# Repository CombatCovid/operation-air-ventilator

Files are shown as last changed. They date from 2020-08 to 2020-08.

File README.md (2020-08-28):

# OperationAIR - Assist In Respiration

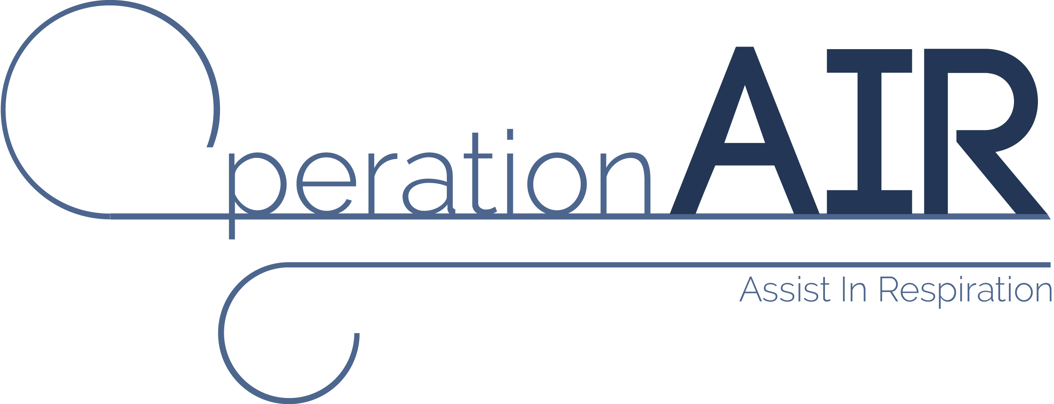
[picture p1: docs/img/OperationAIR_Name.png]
OperationAIR_Name


## OperationAIR: Who are we?

OperationAIR is a student team of Delft University of Technology that developed a simplified ventilator: the AIRone. It was developed as a non-certified, advanced emergency ventilator at times of a national shortage due to the covid-19 pandemic, in close contact with experts from Leiden University Medical Center and Erasmus Medical Center.

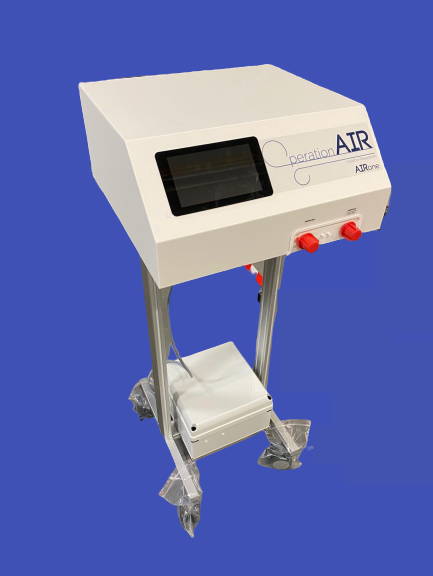
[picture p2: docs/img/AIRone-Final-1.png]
AIRone-Final-1


## AIRone: What is it?

The AIRone operates and functions as a regular, pressure-regulated  ventilator, but with essential functionalities only. In short, it uses a pressurised gas source, reduces the pressure accordingly and delivers  gas to the patient by a set of proportional valves (see below for more  details). Oxygen concentration is regulated using two Mass Flow  Controllers on the gas inlets.

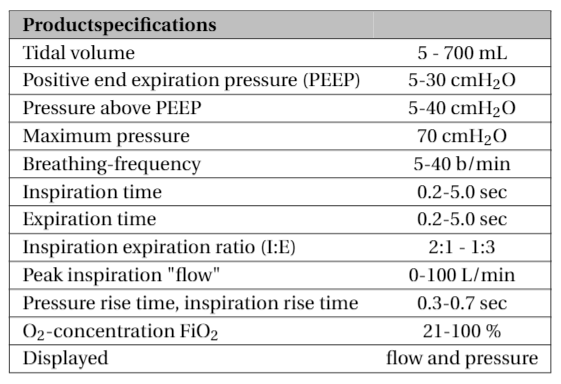
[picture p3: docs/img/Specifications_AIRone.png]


The  AIRone provides positive-pressure ventilation (PPV) for emergency  automatic ventilation, created for the use on adult (suspected) COVID-19 patients who need non-weaned respiratory support to bridge a longer  period of time until conventional ventilation becomes available.

## Adjustable settings

- Inspiratory pressure (Pinsp)
- Positive end-expiratory pressure (PEEP)
- Respiratory rate (RR)
- I:E ratio
- Oxygen concentration(%) (FiO2)

## Project Motivation

The design of the AIRone is final. As national ICU admissions are  dropping large scale production is not necessary. The AIRone is  currently being produced in a small batch to complete the design cycle  and to share this expertise with the international community. Software  engineers will continue to work on an additional module to enable  patient respiration triggers for weaning.

The AIRone was recommended by clinicians to be used at times of  national shortage of certified ventilators. Official approval has not  been obtained, due to the disappeared urgency of emergency ventilators.  Therefore, the safety or efficacy of the AIRone for use in humans has  not been proven. However, thorough design verification was performed  using an advanced artificial test lung. Additionally, design  documentation is under review by a notified body. Also, multiple  usability tests by doctors and nurses lead to the current user-friendly  design.

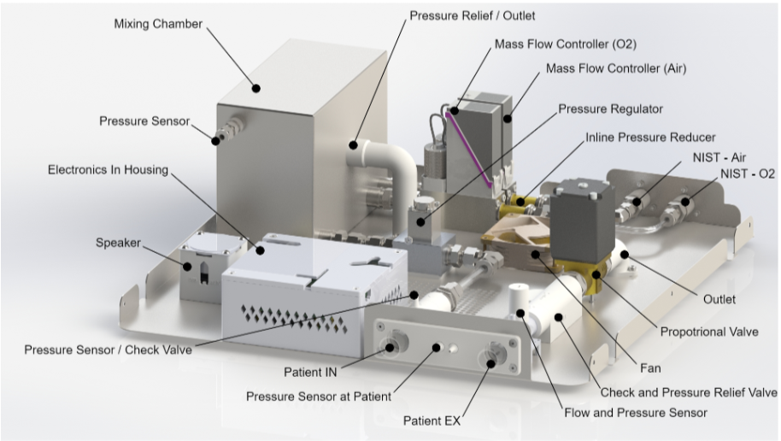
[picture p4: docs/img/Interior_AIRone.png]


## General Working Principle

The AIRone uses pressurized medical air and oxygen that is available  in most Dutch hospitals, reduces it to the required pressure, and  delivers this to the patient using a set of proportional valves that are controlled using a central microcontroller.

The physician can start up the device and use the touchscreen (GUI)  to set ventilation parameters to the desired settings. The GUI will  communicate these setting to the MicroController Unit (MCU). The MCU  then controls all valves to ventilate the patient accordingly.

The AIRone has two male NIST (Non-interchangeable screw thread)  connectors, one for compressed medical air and one for oxygen. The  female counterparts of these connectors should be available in the Dutch hospital and can be connected to the AIRone. The input pressure of both oxygen and compressed air may vary between 4 and 8 bar. In the device,  the oxygen and air pressure is reduced to 4 bar. Two Mass Flow  Controllers (MFCs) are used to control the flow of both gasses into a  mixing chamber. This ensures a highly controlled mixing ratio, having a  gas with the desired oxygen concentration as result. A pressure sensor  in the mixing chamber gives feedback to the MFCs, adjusting their flow  to keep the pressure in the chamber at 650 mbar. As a back-up, a back  pressure regulator ensures the pressure in the chamber will never exceed 1 bar by blowing off air when the pressure is too high.

Downstream of the mixing chamber, a proportional valve regulates the  pressure going into the patient. Generally, the valve will open at the  start of inspiration and close when the pressure at the lungs is at the  desired plateau pressure.  Before the gas mixture flows to the patient  it passes a check valve which blocks flow coming back from the patient.

During expiration, the gas is filtered by a HEPA filter. The gas then passes another check valve, and also a pressure relief valve, which  opens when the pressure in the system rises above 70 cmH20. The gas is  then released to outside the system by another proportional valve that  opens at the beginning of the expiration and closes at the end of the  expiration.

------

**Be aware this design explicitly focuses on use in the Dutch  healthcare infrastructure. Alterations of this design will be needed for local implementation. Please leave your contact information and  additional information in this form so we can discuss matters or offer  advice and support:** https://forms.gle/rWXyzbqTNrqdJqee8

## DISCLAIMER

Licensor means Technische Universiteit Delft and OperationAIR. Licensee means any business, organisation or person using the Licensed Material. Licensed Material means all information pertaining to the last resort ventilator also known as the AIRone

### Intended use

1. The AIRone is a last resort device. It is not designed to replace the currently available, conventional ventilators. The AIRone is a pressure-controlled emergency mechanical ventilation system created for the treatment of COVID-19 patients, who need respiratory support, for who no conventional ventilation machine is available. 
2. The for profit exploitation of the Licensed Material is explicitly prohibited.

### Disclaimer of Warranties and Limitation of Liability.

The Licensor offers the Licensed Material “as-is” and “as-available”, and makes no representations or warranties of any kind concerning the Licensed Material, whether express, implied, statutory, or other. This includes, without limitation, warranties of title, merchantability, fitness for a particular purpose, non-infringement, absence of latent or other defects, accuracy, or the presence or absence of errors, whether or not known or discoverable.

To the extent possible, in no event will the Licensor be liable to Licensee on any legal grounds (including, but not limited to, gross negligence and wilful misconduct) or otherwise for any direct, special, indirect, incidental, consequential, punitive, exemplary, or other losses, costs, expenses, or damages arising out of this Public License or use of the Licensed Material, even if the Licensor has been advised of the possibility of such losses, costs, expenses, or damages.

The disclaimer of warranties and limitation of liability provided above shall be interpreted in a manner that, to the extent possible, most closely approximates an absolute disclaimer and waiver of all liability.

## Project Organization

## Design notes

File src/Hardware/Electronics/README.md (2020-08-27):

# Electronics and firmware for Operation Air Ventilator

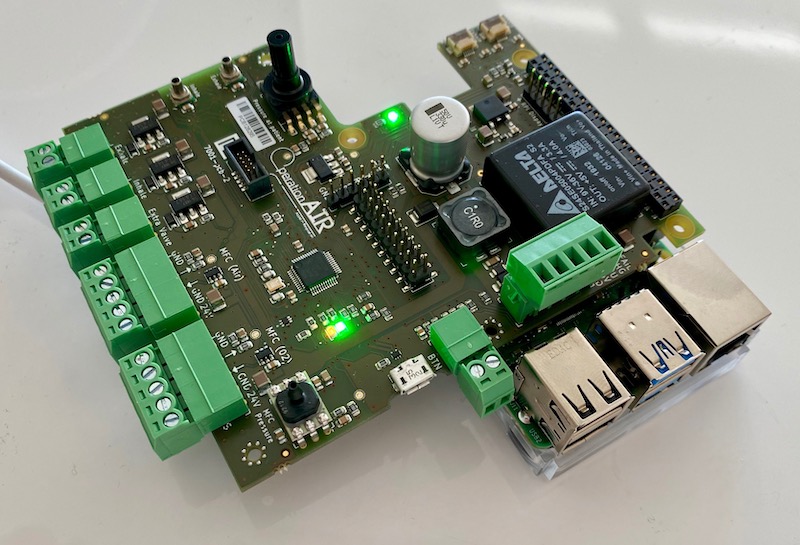
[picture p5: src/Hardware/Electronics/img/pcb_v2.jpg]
OperationAir PCB


The electronics for the Operation Air AIROne is comprised of a custom developed PCB with a LPC11U37 microcontroller stacked on top of a Raspberry Pi 4 (Model B).

This repository contains the electronic designs for the PCB and the accompanying firmware.

The Pi talks to the microcontroller over UART using a [custom binary protocol](firmware/README.md#uart-communication-protocol).

Contact info@interay.com for assembled, tested and programmed ready for use boards.

## License

Copyright (c) 2020 TU Delft. All rights reserved.

Licensed under the [Apache 2.0](LICENSE) license.

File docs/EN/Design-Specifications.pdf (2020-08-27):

| Design Specifications
OPERATIONAIR: OperationAIR (OperationAIR) | Date: 2020/04/29 14:28:23
Document: 1 | Page: 1 / 12

All dates and times are in the project’s default time zone and formatting.

### 1. TABLE OF CONTENTS

### 2. DESIGN SPECIFICATIONS

### 2.0.1. Features

SPEC-31 Ventilation mode
Device has a Pressure Controlled Ventilation (PCV) mode

SPEC-46 Usability user-interface
The user-interface is intuitive, simple, and straightforward to use

SPEC-34 Visualized measurements
Volume [mL], pressure [cm H2O] and flow [L/min] must be visualized on the device's screen in graphs or as numbers

SPEC-150 Instructions For Use
Instructions For Use (IFU) are supplied with every device and are available for download online

SPEC-42 Compatibility with standard hospital equipment
The device is compatible with standard hospital equipment according to NEN-EN-ISO 5359:2014/A1:2017 and ISO 5361:2016

SPEC-141 Inspiratory hold

(OperationAIR) | Date: 2020/04/29 14:28:23
Document: 1 | Page: 2 / 12

The device can perform an inspiratory hold to determine Plateau Pressure.
When the button is pressed, respiration stops at the peak of the inspiration, while measuring the pressure in the system. When the user lets go of the button, respiration instantly starts again

SPEC-156 Expiratory Hold
The device can perform an expiratory hold to determine PEEP.
When the button is pressed, respiration stops at the end of the expiration, while measuring the pressure in the system. When the user lets go of the button, respiration instantly starts again

SPEC-73 Interruption of power supply
Device is equipped with a UPS to continue ventilation in case of power failure

SPEC-60 Breaks
The device has breaks that shall be used when the device doesn't need to be moved

SPEC-27 Flow Sensor
Device must be equipped with a flow sensor

SPEC-153 HEPA filter
Device can be equipped with a HEPA filter

SPEC-25 HME-filter
Device must be equippable with an ISO 9360-1:2000 certified HME-filter and should be equipped with such a HME filter. These HME filters are disposable and must be changed with every patient.

SPEC-166 Ventilator
The device has a ventilator to mix potential leaking oxygen with surrounding air

### 2.0.1.1. Ventilation Parameters

SPEC-155 Ppeak setting
The pressure above PEEP can be set by the user in the range 5 to 40 cm H2O, in intervals of 1 cm H2O

(OperationAIR) | Date: 2020/04/29 14:28:23
Document: 1 | Page: 3 / 12

SPEC-35 PEEP setting
The positive end-expiratory pressure (PEEP) must be adjustable between 5 and 30 cm H2O, and the PEEP can be adjusted per 1 cm H2O

SPEC-20 Breathing rate setting
The breathing rate can be set by the user between 5/min and 40/min

SPEC-38 I:E ratio setting
Inspiratory:expiratory ratio must be adjustable between 2:1 and 1:3

SPEC-37 FiO2 setting
The FiO2 must be adjustable per 5%

### 2.0.1.2. Alarms

SPEC-6 Alarm for Inspiratory O2 concentration (FiO2)
An alarm for a too high or too low fractional inspiratory oxygen level.

SPEC-9 Alarm for positive end-expiratory pressure (PEEP)

SPEC-8 Alarm for Tidal volume (Tv)
Provide an alarm when the tidal volume is outside the accepted range set by the user.

SPEC-89 Alarm for Peak Pressure (Ppeak)

SPEC-87 Alarm for Apnea or disconnect
Alarm when inspiratory or expiratory airflow circuit is blocked or disconnected

SPEC-84 Alarm for empty battery
Device issues a warning when battery is almost empty.

(OperationAIR) | Date: 2020/04/29 14:28:23
Document: 1 | Page: 4 / 12

SPEC-19 Clear explanation per alarm on GUI
When an alarm or warning is issued, the device must clearly indicate what alarm is issued

### 2.0.2. Performance

SPEC-95 Error margins: Tidal Volume
Maximum error between internally and externally measured Tidal Volume is 5%

SPEC-94 Error margins: I:E ratio
Maximum error between set and measured I:E ratio is 0.05

SPEC-93 Error margins: FiO2
Maximum error margin between measured and set FiO2 is 5%

SPEC-92 Error margins: breating rate
Maximum error between measured and set breating rates is 1/min

SPEC-90 Error margins: Lung/airway pressure
Maximum pressure loss between device and patient lungs is 10 cm H2O

SPEC-36 FiO2 range
Device is able to provide a FiO2 between 21% and 100% at 5% accuracy.

SPEC-26 Tidal Volume
Device is able to provide tidal volumes between 300 and 700 mL

SPEC-40 Inspiratory Flow
The inspiratory flow that the device delivers to the patient has a peak value of at least 1.5 L/s

SPEC-118 Reliability
Under the same settings the device should give the same output.

(OperationAIR) | Date: 2020/04/29 14:28:23
Document: 1 | Page: 5 / 12

SPEC-128 14 day reliability
Device must be able to operate continuously for at least 14 days, preferably more. Specify expected durability in documentation.

### 2.0.3. Safety

SPEC-29 Peak pressure
Device must keep the peak pressure always below 70 cm H2O

SPEC-146 Flow sensor shielding
Flow sensor is electrically shielded, all components near the flow sensor are non-conductive or sufficiently grounded

SPEC-144 Airflow materials
All components through which inspiratory air can flow are
- biocompatible
- oxygen compatible
- clean
- non-porous
- have a high auto-ignition temperature

SPEC-129 Robustness
The device is able to withstand continous use and transport

SPEC-126 Cleaning and disinfection
The device and its materials are able to withstand regular cleaning and disinfection

SPEC-120 Alarms are easy to understand and intuitive
The alarms are made according to ISO 60601-1-8

SPEC-113 Impairment of cooling

(OperationAIR) | Date: 2020/04/29 14:28:23
Document: 1 | Page: 6 / 12

The medical device must remain safe during the failure of cooling systems, f.e. when ventilation openings are covered.

SPEC-103 No air leakage
The device may not leak air or oxygen

SPEC-100 External exhaust outlets
External exhaust outlets are placed in the bottomplate of the device, where they cannot be blocked by walls or other objects

SPEC-99 Temperature of inspirated air
Temperature of the inspirated air and the tubes through which the air flows must be below 30 degrees celcius

SPEC-85 High Voltage circuit outside casing
The high voltage circuitry shall be separated from the high O2 network

SPEC-83 Testing of the fail-safe valve during production
The correct functioning of fail-safe valves shall be tested during production

SPEC-80 Housing impact test
The housing must withstand an impact of a solid smooth steel ball, approximately 50 mm in diameter and with a mass of 500 g ± 25 g, falling freely from 1,3 m height once onto each relevant part of the test sample or swinging like a pendulum, that drops through a vertical distance of 1,3 m, against vertical surfaces. The test is not applied to flat panel displays.

SPEC-79 Housing mechanical resistance
The housing must be able to withstand forces of 250 N without breaking

SPEC-72 Leakage current testing
Since the protective earthing is accessible, leakage current is considered touch current, and the acceptance level for leakage current is <100 uA.

(OperationAIR) | Date: 2020/04/29 14:28:23
Document: 1 | Page: 7 / 12

SPEC-71 Patient leakage current
The values for patient leakage must not exceed 50 uA

SPEC-70 Touch current
Touch current from or between parts of the medical device within the patient environment must not exceed 100 μA. Leakage current from accessible outer surfaces of the equipment is also considered to be touch current.

SPEC-67 Acoustic Energy
The acoustic energy emitted by the device shall not exceed 80 dB during worst case normal use

SPEC-65 Sharp edges
The device shall have no sharp edges that could lead to tearing of protective gloves or the skin

SPEC-63 Instability unintended force
The device must be able to withstand unintended forces without tipping over.

SPEC-62 Instability incline surface
Device must not overbalance when placed on an inclined surface at 10 degrees from the horizontal

SPEC-143 Visibility User Interface
The user interface can be easily used and is clearly visible when wearing protective eyewear

SPEC-145 Watchdog program
A watchdog program checks every second if every part of the software does what it is supposed to do. When a part of the software malfunctions, the watchdog will instruct a different part to reboot the malfunctioning part.

SPEC-53 Power Supply
The device shall use a IEC 60601-1 certified mains supply adapter for connection to a 230V AC supply mains.

(OperationAIR) | Date: 2020/04/29 14:28:23
Document: 1 | Page: 8 / 12

SPEC-32 Expirated air
The expirated air must always be separated from inpiratory air

SPEC-44 Non-conductive exterior casing
The exterior casing of the device must be made of a non-conductive material or the material must be grounded

SPEC-45 Protective equipment
The device can be used by users wearing personal protective equipment such as gloves and protective glasses

SPEC-23 Protected off switch
The off switch is protected for accidental pressing

SPEC-22 The O2 and air input connectors
The O2 and air input connectors comply with ISO 18082:2014 and are non-interchangeable

SPEC-18 Battery use warning
When power supply fails and the device starts running on battery power, an alarm is issued

SPEC-5 Pressure relief valve
The device has a mechanical pressure relief valve that opens at 70 cm H2O

SPEC-4 Calibrate sensors during assembly
All pressure sensors and the flow sensor must be calibrated during assembly

SPEC-2 Robustness internal components
All internal components are tightly secured to the bottomplate

SPEC-1 Ingress of water
The exterior casing is spraying water proof (comparable with IP-22)

(OperationAIR) | Date: 2020/04/29 14:28:23
Document: 1 | Page: 9 / 12

SPEC-162 Installation Verification
Installation Verification is performed after assembly:
- Serial numbers of components have to be registered
- The power supply has to be inspected
- The device has to be inspected visually
- Pressure sensors have to be inspected
- The device has to be turned on and off and power down has to be inspected
- Electrical safety has to be inspected
- Sensors, valves and output have to be tested
- Gas system integrity has to be tested.

### 2.0.4. Information provided to the user

### 2.0.4.1. IFU

SPEC-152 IFU: regulatory requirements
The medical device must be accompanied by an IFU with referral address of the manufacturer. These documents can be shared electronically or in printing. Additionally the following must be included:
- a list of all items that are part of the medical device,
- instructions for installation, assemblation and modification,
- instructions for cleaning, desinfection, sterilization of each item or the entire device,
- the safety measures that should be applied during installation,
- which parts are suited for the patient environment,
- Measures that must be applied during preventive maintenance,
- the permissible environmental conditions of use of the ME SYSTEM including conditions for transport and storage,
- advice to the RESPONSIBLE ORGANIZATION: – to carry out all adjustment cleaning, sterilization and disinfection PROCEDURES specified therein;
- advice to the RESPONSIBLE ORGANIZATION: – that the assembly of ME SYSTEMS and modifications during the actual service life require evaluation to the requirements of this standard.
- the name of the device;
- the manufacturer of the device;
- the adress of the manufacturer;
- Indications and contra-indications,
- intended use and intended user;
- the clinical benefit for the patient;
- the performance characteristics;
- the degree of accuracy for the parameters of the device;
- how to verify if the right accessories are used;
- undesirable side-effects;

(OperationAIR) | Date: 2020/04/29 14:28:23
Document: 1 | Page: 10 / 12
- preperation of the device before use;
- that users must receive a training before using the device;
- information on maintenance and cleaning of the device and accessories;
- information on cleaning and disinfection between the use on different patients;
- all the warnings that will lead to malfunction of the device and/or changes in the working of the device that will lead to risks to the patient. This will include enviromental changes, like diagnostic or therapeutic procedures;
- how the device can safely be disposed;
- publication or printing date with version number;
- that SAE's must be meantioned to the manufacturer;
- how to safely use the software on the device.

SPEC-47 IFU: intended use
IFU contains an explanation of the intended use of the device

SPEC-13 IFU: Device not for use during transport
Warning in IFU that the device may not be used during patient transport

SPEC-14 IFU: Check device before use
Warning in IFU that device functionality must be checked before use

SPEC-98 IFU: Do not use when damaged
Instructions For Use mention that the device must be inplugged when damaged, for example after a fall or when other parts are visibly damaged.

SPEC-117 IFU: turn off device before unplugging
Warning in the IFU that the device has to be turned off on the user interface before cutting the power

SPEC-134 IFU: ventilator settings
The IFU mentions the upper and lower limits of the ventilation settings

SPEC-135 IFU: Explanation of the alarms
The alarms, their causes, and how to deal with them should be clearly explained in the IFU.

(OperationAIR) | Date: 2020/04/29 14:28:23
Document: 1 | Page: 11 / 12

SPEC-137 IFU: HEPA filter
The IFU contains instructions about the use of the HEPA-filter

SPEC-51 IFU: Instructions for correct and safe maintanance
The instructions for use shall state instructions for correct and safe maintenance

SPEC-138 IFU: alarm boundaries
The IFU explains how to set the upper and lower alarm boundaries and mentions the alarm limits

SPEC-17 Training and clear IFU for the users
IFU and training materials are developed and validated in collaboration with medical doctors and nurses. IFU warns that the device can only be used by trained users.

SPEC-49 IFU: checked by experts
The Instructions for use shall be reviewed by both internal quality control and external experts

### 2.0.4.2. Label

SPEC-151 Label: regulatory requirements The label on the device will contain:
- the device name;
- a serial number;
- the manufacturer with address;
- the manufacturing date, as part of the serial number or seperatly;
- immediate warnings with icons.
All will be written in text or official icons.

SPEC-64 Emergency use sticker
The device has a clear warning sticker with the text that it is a device which is meant for use ONLY in emergencies on COVID-19 patients.

(OperationAIR) | Date: 2020/04/29 14:28:23
Document: 1 | Page: 12 / 12

SPEC-115 Emergency number on label
A telephone number is shown on the label that can be called when assistance is required

SPEC-133 HEPA filter warning sticker
Sticker above the expiratory air connector of the device with the text that the HEPA filter must be placed before use

SPEC-61 Do not push warning
The label has a warning to not push (ISO 7010 P017).

SPEC-154 Fire warning sticker
The label contains a warning to keep device away from open fire

SPEC-148 Device label
The label is placed on the device and must be visible from the point of use by the user.

SPEC-130 Intuitive for use - training
Must not require more than 30minutes training for a doctor with some experience of ventilator use.

SPEC-48 Vocabulary and Semantics
Always use the standard nomenclature as defined in BS ISO 19223:2019 regarding lung ventilators and related equipment: Vocabulary and semantics.

SPEC-167 Open Source
All documentation of the AIRone is online available for free. When documentation goes missing or is unreadable, the user can refer to the online database.

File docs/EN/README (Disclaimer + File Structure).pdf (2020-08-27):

## README

DISCLAIMER

Licensor means Technische Universiteit Delft and OperationAIR

Licensee means any business, organisation or person using the Licensed Material

Licensed Material means all information pertaining to the last resort ventilator also known as the AIRone

Intended use

1. The AIRone is a last resort device. It is not designed to replace the currently available, conventional ventilators. The AIRone is a pressure-controlled emergency mechanical ventilation system created for the treatment of COVID-19 patients, who need respiratory support, for who no conventional ventilation machine is available.
2. The for profit exploitation of the Licensed Material is explicitly prohibited.

Disclaimer of Warranties and Limitation of Liability.

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

## OSF File Structure - OperationAIR

- README (Disclaimer + File Structure)
- General
- Instructions for Use
- Service Structure
- Team Structure
- Tips and Pitfalls
- Hardware
- AIRone Assembly
- Architecture
- Bill Of Materials
- Design Specifications
- Design Verification
- Technical Manual
- Assembly Manuals
■ 1. Work Instructrion Subassembly 1 - MFC-AIR_EN
■ 2. Work Instruction Subassembly 2 - MFC-OXYGEN_EN ■ 3. Work Instruction Subassembly 3 - Mixing chamber_EN ■ 4A. Work Instruction Subassembly 4A - Swagelok_EN ■ 4B. Work Instruction Subassembly 4B - 3D blocks_EN ■ 4C. Work Instruction Subassembly 4C - Insp_Tract_EN ■ 5. Work Instruction Subassembly 5- Expiratory Tract_EN ■ 6. Work Instruction Subassembly 6 - PCB + wiring_EN
■ 6B. Work Instruction Subassembly 6B- SD_software_EN ■ 6C. Work Instruction Subassembly 6C- SD_connection_EN ■ 7. Work Instruction Subbassembly 7 - Hood_EN
■ 8. Work Instruction Subassembly 8 - Bottom plate_EN
■ 9. Work Instruction Subassembly 9 - Trolley_EN
■ 10. Work Instruction Subassembly 10 -Connect components _ Components to plate_ EN
■ 11. Work Instruction Subassembly 11 - Wiring_EN
■ 12. Work Instruction Subassembly 12 - Bottom plate + trolley_EN ■ 13. Work Instruction Subassembly 13 - hood_to_base_EN
■ 14. Work Instruction Subassembly extra - speaker_EN
- Hardware Overviews
■ Connector-G1-2_22mm
■ Connector-G3_8-22mm
■ Overview_Interior
■ Overview_Interior_3D_Printing ■ Overview_Exterior
■ Selection_Cover_Closed
■ Selection_Cover_EX
■ Selection_Inspiratory_EX ■ Selection_Speaker_Double

- 3D Printing
■ 3D Printing Overview
■ FDM_Electronics_Housing_1 ■ FDM_Electronics_Housing_2 ■ FDM_EX_Pressure_Relief_Plate ■ FDM_Flow_Sensor_Cap
- Renders
■ Airchain
■ Airchain_EX
■ Cap_Back
■ Cap_Front
■ Expiration
■ Expiration_EX
■ Exterior
■ Exterior_Front_Back
■ Inspiration
■ Inspiration_3Dprint
■ Inspiration_3Dprint_EX
■ Inspiration_EX
■ Inspiration_incl_3Dprint ■ Interior
■ Interior_Exterior
■ Interior_Top
■ Interior_Trolley
■ NIST_Bottom
■ NIST_Bottom_EX
■ NIST_Bottom_Rear
■ O2chain
■ O2chain_EX
■ PCB
■ PCB_EX
■ Pin
■ Pin_EX
■ Plate
■ Plate_AIR
■ Plate_Connections
■ Plate_Expiration
■ Plate_Fan
■ Plate_Inspiration
■ Plate_O2
■ Plate_Patient_Connection
■ Plate_Patient_Connection_EX ■ Plate_Tank
■ Plate_Tank02
■ Plate_Top
■ Speaker
■ Speaker_EX

■ Tank
■ Tank_EX
■ Trolley
■ Trolley_EX
- Software
- Human Interface
■ Github Human Interface
- Electronics
■ Github Electronics

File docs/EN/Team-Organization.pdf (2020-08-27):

Management:
Professor
Team manager (student)
3 Subteam leaders

Phase One (Week 1 to 3.5)

Team Leader: (external framework, valves, testing, O2) | Vice-Team Leader: (software, GUI, 3D and control)
1 | 1
External framework & Connections | Mixing chamber
3D ontwerpers | Test team
Software design | Interface/GUI
Control (systems) | Valves
Team members: valves | Team members: external framework | Team members: 3D team | Team members: software
3 | 3 | 6 | 3
Team members: O2 sensor | Team members: test team | Team members: control | Team members: interface/GUI
1 | 4 | 4 | 2

Design subteams

## Design

Phase One (Week 1 to 3.5) | Realisation

Team Leader
1
Production | Implementation | Distribution
Explore production facilities | Manual | Packaging parts/device
Find manufacturers for parts | Maintenance | Shipment
Who will assemble the product? | Education of clinical staff | Contact with national center coordination center for distribution
Where do we assemble? | Installation plan | Provide (or advise on) compatible disposables to be used with device
Sterilization? | Control of device
Post-production quality check
Team members | Team members | Team members
2 | 3 | 3

Phase One (Week 1 to 3.5) | PR & Legal & Finance

Team Leader
1
Media & PR | Finance | Legal
Put out requests for parts critical of elivery | Calculate cost/device | Risk management
Maintain media contact | Plan finance for upscaling | Risk mitigation plan
Update social media platforms and create website | | Test protocol
Create platform to spread information about our project | | Test plan
| | Distribute responsibility, reliability and authorities
Team members | Team members | Team members
2-4 | 2 | 5

Management
Professor
1 Team manager (student)
3 Subteam leaders
1 Workshop manager

Phase Two (Week 3.5 to now)

Team leader: 1 (Hardware) | Team leader
Vice Team leader: 1 (Software) | 1
Team | Development | Troubleshooting | Support team | Durability monitoring
| Software updates | Be present in clinic during first use | Answer emergency phone | Monitor quality of devices
| Control systems update | Standby for troubleshooting | Answer service phone | Monitor life cycle parts
| 3D design update | Name incidents and propose solutions | Collect incident reports | Create service plan
| Patient triggers | Install devices hen first used | Post reports and update user FAQ | Test seperate models on durability
| Hardware update | Quickfix software bugs | Overview team member part experts
| | | pass user feedback to the right sub team
Team members | Team members | Team members | Team members
14 | 8 | 5 | 6

Phase Two (Week 3.5 to now)

Media & PR | Open Source | International contacts
Put out requests for parts critical of elivery | Document project | Provide consultation to other teams
Maintain media contact | Open Source | Answer questions to other initiatives
Update social media platforms and create website
Create platform to spread information about our project
Team members | Team members | Team members
2 | 5 (part time) | 5 (part time)

Phase Two (Week 3.5 to now)

Team leader
1
Supplychain management | Logistics | Training coordination
Maintain contact with part manufacturers | Overview ventilator locations | Train the education team
Mediate between assebly company and part manufacturers | Overview locations of education and service teams | Update user manual
Plan deliveries | Overview logistics of part delivery | Update education material
Solve problems regardng delayed parts | Overview transport of teams to hospitals | Coordinate post-market training
Maintain contact with Dutch health authorities | Maintain contact with national distribution network for health supplies
Create traceability plan for assembly
Team members | Team members | Team members
4 | 3 | 3

Phase Two (Week 3.5 to now)

Training team | Production | Finances
Give training to users | Assist with assembly | Request funding of funds
| | Request funding of grants
Team members | Team members | Team members
9 | 7 | 1
| Extra members during start-up fase
| 6

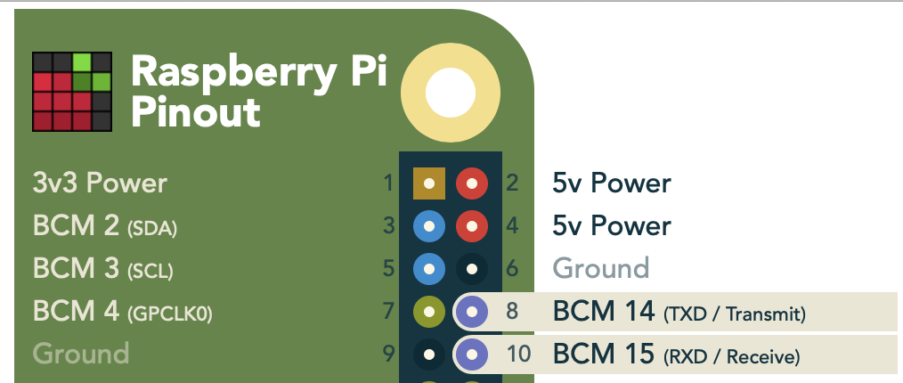
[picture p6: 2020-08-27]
src/Hardware/Electronics/blinky/img/uart_pinout.png

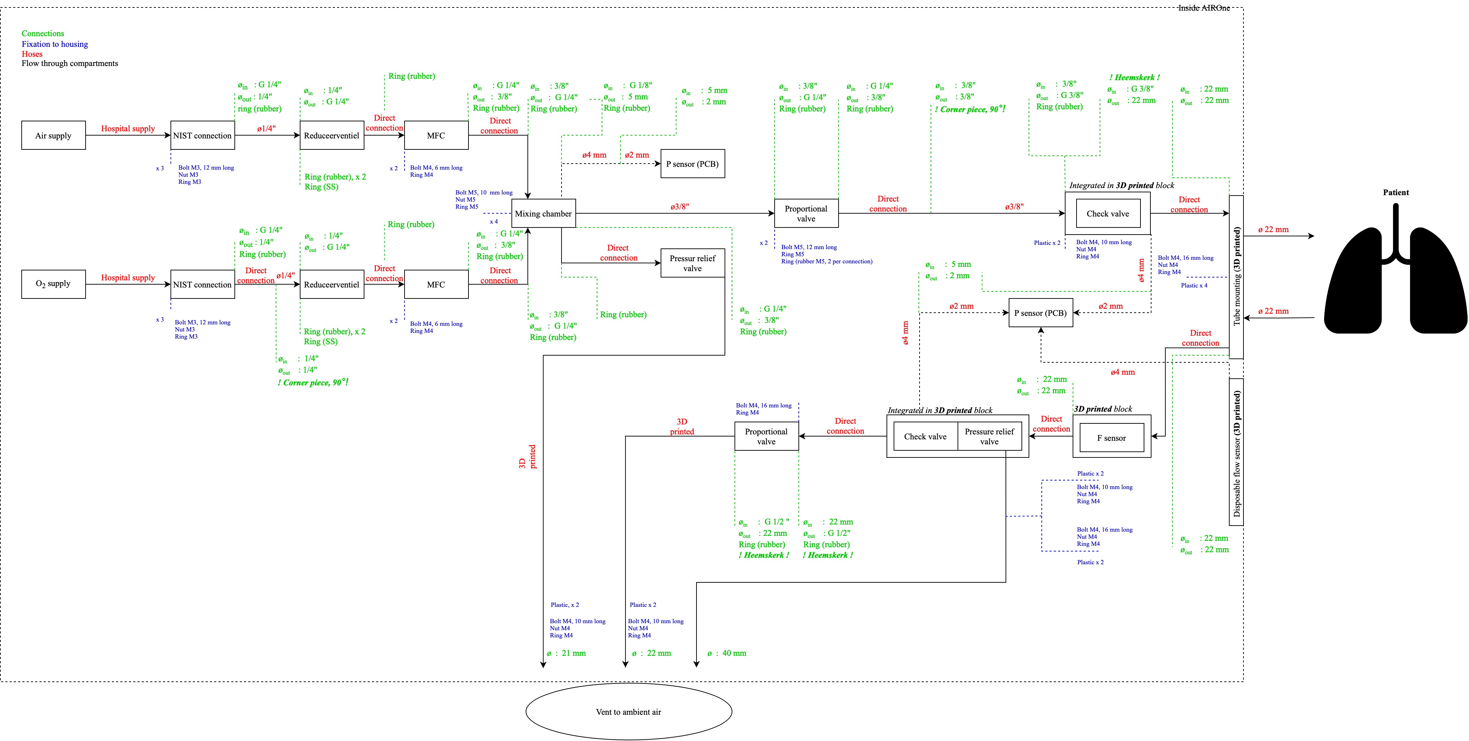
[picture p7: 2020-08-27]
docs/img/Architecture.jpg

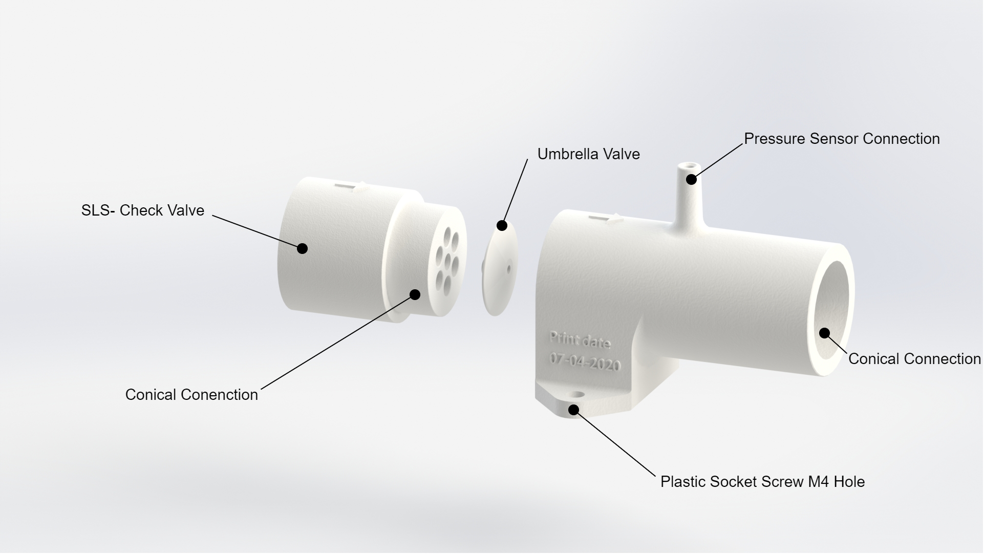
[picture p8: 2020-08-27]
src/Hardware/Hardware-Overview/Selection_Inspiratory_EX.png

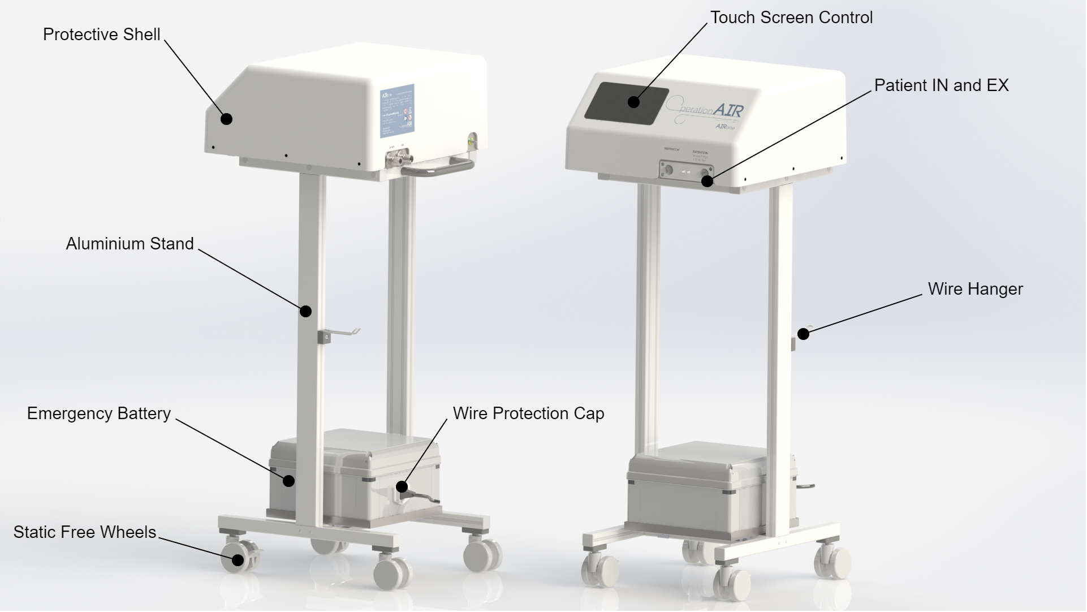
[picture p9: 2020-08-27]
src/Hardware/Hardware-Overview/Overview_Exterior.png

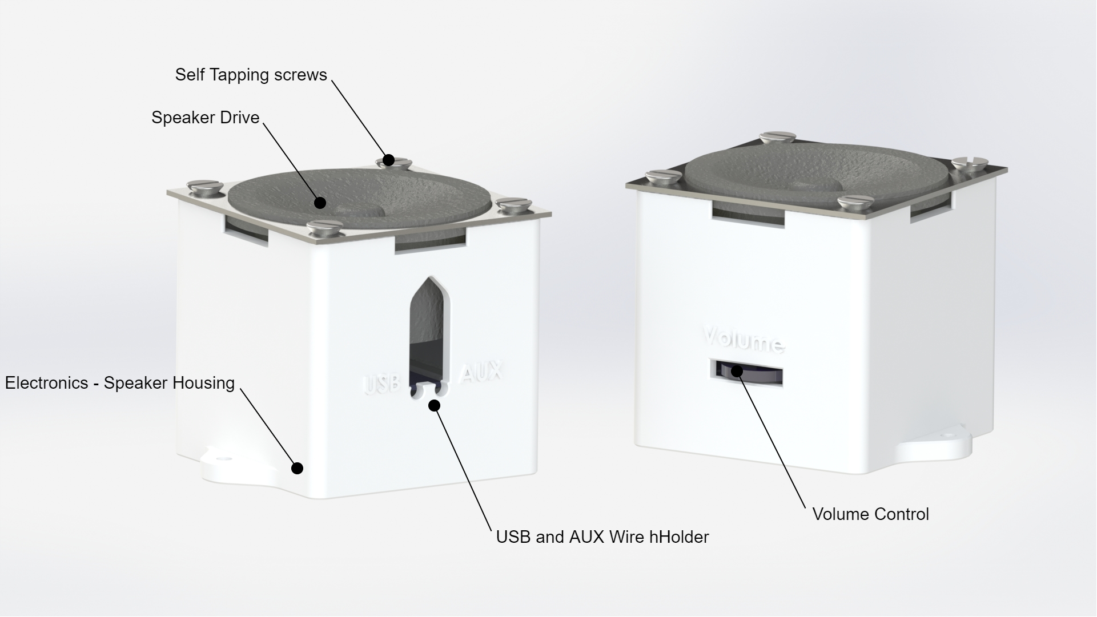
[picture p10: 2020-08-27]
src/Hardware/Hardware-Overview/Selection_Speaker_Double.png

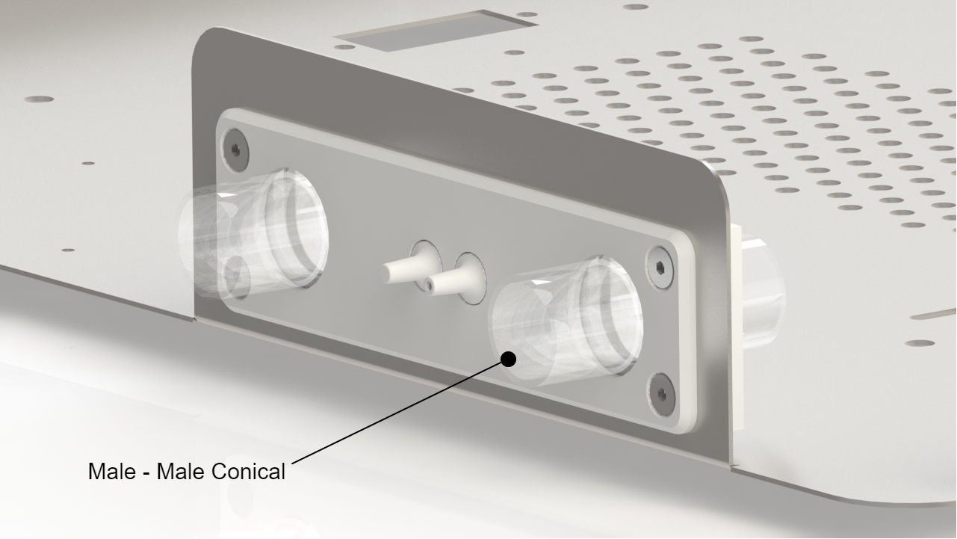
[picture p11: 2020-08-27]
src/Hardware/Hardware-Overview/Selection_Cover_Closed.png

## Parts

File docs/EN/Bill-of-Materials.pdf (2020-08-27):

BOM Level | Part-ID | Part Name | Quantity | Technical Requirement Notes | OperationAIR Suppliers
0 | 0 | AIRone, Packed | 1 | Mechanical ventilator
1 | 1 | Electronic control system | 1
2 | 1.1. | Assembled PCB | 1 | Link to Github: https://github.com/OperationAIR/electronics See the Technical Manual (4.17) for detailed specifications | Interay Solutions
3 | 1.1.1. | Pressure Sensors | 1 | | Interay Solutions
4 | 1.1.1.1 | Pressure Sensor 1 | 1 | MPVZ5010GW6U See the Technical Manual for detailed specifications | Interay Solutions
4 | 1.1.1.2 | Pressure Sensor 2 | 1 | MPRLS0001PG0000SA See the Technical Manual for detailed specifications | Interay Solutions
4 | 1.1.1.3 | Pressure Sensor 3 | 1 | ABPDANT015PGAA5 See the Technical Manual for detailed specifications | Interay Solutions
3 | 1.1.2 | PCB printing parts | 1 | | Interay Solutions
3 | 1.1.3 | PCB Base Plate | 1 | | Würth Elektronik GmbH & Co. KG
3 | 1.1.4 | Software | 1 | | Jitter
2 | 1.2 | Raspberry Pi | 1 | Raspberry Pi 4 4G Model B See the Technical Manual (4.18) for detailed specifications | RS online
2 | 1.3 | Raspberry Pi Touchscreen Display | 1 | Raspberry Pi 7" 800x480 DSI Touchscreen Display See the Technical Manual (4.18) for detailed specifications | RS online
2 | 1.4 | Micro-SD Card (16G) | 1 | Kingston 16 GB MicroSDHC Card Class 10, UHS-1 U1 | RS online
2 | 1.5 | High pressure hoses | 1
3 | 1.5.1 | High pressure hose 1 | 2 | 4mm, PVC 4x6mm | Landfeld
3 | 1.5.2 | High pressure hose 2 | 1 | 4mm, 6x1 mm | Festo
3 | 1.5.3 | High pressure hose 3 | 3 | 2mm, 3x0.5mm | Festo
3 | 1.5.4 | High pressure hose connector | 3 | Adapter, PP, Male luer to 1/16" barbed | Interscience
2 | 1.6 | Cables | 1
3 | 1.6.1 | Jumper Cable | 1 | 6876 FFC, 0.5mm Pitch, 6 Way, 200mm Cable Length, 500 mA, 60 V ac | RS online
3 | 1.6.2 | Flex cable Raspberry Pi to Camera Board | 1 | 30 cm, MPN: 2283 | Kiwi electronics
3 | 1.6.3 | Cable PCB to Solenoid Control Valve | 1 | 10cm, 0.3255mm2 (22 AWG), 2 cable cores
3 | 1.6.4 | Cable PCB to ARMAND klep | 1 | 40cm, 0.3255mm2 (22 AWG), 2 cable cores
3 | 1.6.5 | Cable PCB to Raspberry Pi | 1 | USB IDC connection cable, 45cm, 24 AWG, 5 cable cores, F-F connections
3 | 1.6.6 | Cable PCB to Power cable | 1 | 20cm, 1.3087 mm2 (16 AWG), 5 cable cores
2 | 1.7 | Aluminum tape | -
2 | 1.8 | Ferrite cores | 1
3 | 1.8.1 | Ferrite core: cable PCB to MFC | 1 | TDK Openable Ferrite Clamp, 16.5 Dia. x 30mm | RS online
3 | 1.8.2 | Ferrite core: cable PCB to flow sensor | 1 | 28R0480-000 - Ferrite Ribbon Core, 190 ohm, 100 MHz, 8.0mm x 1.0mm | Farnell
3 | 1.8.3 | Ferrite core: cable PCB to Raspberry Pi | 1 | Wurth Elektronik 4 W 1500 Ferrite Sleeve, Inner dimensions:18.8 x 1.1mm | Farnell
2 | 1.9 | Grounding cable | - | Grounding for cables 30cm, 2.5mm2 (AWG14)
2 | 1.1 | Heatshrink | - | 1 mm diameter
2 | 1.11 | Speaker | 1 | Nedis - CSPR10020BK See the Technical Manual (4.19) for detailed specifications | TodoTipo
2 | 1.12 | Grounding | 1 | | Medical IT Shop
3 | 1.12.1 | Grounding pin | 1 | Potential Equalization Pin Built in Plug Complete 6/15 | Medical IT Shop
3 | 1.12.2 | Grounding cable | 1 | DIN 42801, PE Connection Lead STD 6mm² / 3m | Medical IT Shop
2 | 1.13 | Power Supply | 1 | See the Technical Manual (4.23) for detailed specifications
3 | 1.13.1 | Power Cable | 1 | Power Cable C13 | Medical IT Shop
3 | 1.13.2 | Transformer | 1 | Meanwell 200W Reliable Green Medical Power Supply, RPS-200-24 | Telerex

3 | 1.13.3 | UPS | 1 | Meanwell Supply40ADC UPS Module, DR-UPS40 | Telerex
3 | 1.13.4 | Battery | 1 | DYN/DAS12-2.2 | NS
1 | 2 | Housing | 1 | See the Technical Manual (4.22) for detailed specifications
2 | 2.1 | Metal bottom plate | 1 | Custom design | Kasteelmetaal
2 | 2.2 | Top cap | 1 | Custom design | Formit
2 | 2.3 | Sealing cap | 1 | Intersurgical reference number: 1978000 | Merkala
2 | 2.4 | Chassis | 1 | Custom design | Item
2 | 2.5 | Stickers | 1 | Custom design | Sticker Koning
3 | 2.5.1 | Technical Sticker | 1 | Custom design | Sticker Koning
3 | 2.5.2 | Safety Sticker | 1 | Custom design | Sticker Koning
3 | 2.5.3 | Inlet / outlet stickerset | 1 | Custom design | Sticker Koning
3 | 2.5.4 | Logo sticker | 1 | Custom design | Sticker Koning
1 | 3 | Mechanic | 1
2 | 3.1 | Mass flow controler | 1 | | Bronkhorst
3 | 3.1.1 | MFC AIR including cables | 1 | OAD-001F See the Technical Manual (4.3) for detailed specifications | Bronkhorst
3 | 3.1.2 | MFC O2 including cables | 1 | OAD-002F See the Technical Manual (4.3) for detailed specifications | Bronkhorst
2 | 3.2 | Gas pipe fittings | 1 | See the Technical Manual (4.23) for detailed specifications | Swagelok
3 | 3.2.1 | G1/4" to 3/8" tube ftting | 6 | SS-600-1-4RS | Swagelok
3 | 3.2.2 | G1/4" to 1/4" tube fitting | 4 | SS-400-1-4RS | Swagelok
3 | 3.2.3 | G3/8" to 3/8" tube fitting | 1 | SS-600-1-6RS | Swagelok
3 | 3.2.4 | Elbow 1/4" | 1 | SS-400-2R-4 | Swagelok
3 | 3.2.5 | Elbow 3/8" | 1 | SS-600-2R-6 | Swagelok
3 | 3.2.6 | G1/8" Gasket | 1 | SS-2-RS-2V | Swagelok
3 | 3.2.7 | G1/4" Gasket | 16 | SS-4-RS-2V | Swagelok
3 | 3.2.8 | G3/8" Gasket | 1 | SS-6-RS-2V | Swagelok
3 | 3.2.9 | G1/2" Gasket | 1 | SS-8-RS-2V | Swagelok
3 | 3.2.10 | G1/4" to 3/8 tube fitting | 2 | SS-6-TA-1-4RS | Swagelok
3 | 3.2.11 | G1/8" to 6mm | 1 | SS-6M0-1-2RS | Swagelok
2 | 3.3 | PFA Tubing | 1 | | Swagelock
3 | 3.3.1 | PFA Tubing 3/8" | - | PFA_T6_062_100 | Swagelock
3 | 3.3.2 | PFA tubing 1/4" | - | PFA-T4-047-100 | Swagelock
2 | 3.4 | Solenoid Control Valve (Expiratory) | 1 | Type 2875 - Direct-acting 2 way standard solenoid control valve See the Technical Manual (4.16) for detailed specifications | Burkert
2 | 3.5 | Spring loaded overpressure relief valve | 1 | 70-250 mbar, Part number 5046, DN40KF See the Technical Manual (4.15) for detailed specifications | Demaco
2 | 3.6 | Safety Valve | 1 | Mini safety valve G 1/4", 1 - 4 bar, Brass, Item number: SVM 14-4 See the Technical Manual (4.6) for detailed specifications | Landefeld
2 | 3.7 | Umbrella Valve | 2 | UM 215.002 SD See the Technical Manual (4.8+4.14) for detailed specifications | Minivalve
2 | 3.8 | SLS 3D prints | | Printed with Nylon 12
3 | 3.8.1 | Patient IN | 1 | Custom design: housing umbrella valve | Shell
3 | 3.8.2 | Patient OUT | 1 | Custom design: housing umbrella valve, pressure sensor, pressure relief | Shell
3 | 3.8.3 | Check valve mount | 2 | Custom design: mount for umbrella valve, placed on Patient IN/OUT | Shell
3 | 3.8.4 | Pressure tubes | 1 | Custom design: mount for pressure tubes, placed in tube doublemount | Shell

3 | 3.8.5 | Flow sensor holder | 1 | Custom design: housing flowsensor | Shell
3 | 3.8.6 | EndTube | 1 | Custom design: leads expiratory air outside the device | Oceanz
3 | 3.8.7 | Tankout | 1 | device | Oceanz
2 | 3.9 | Diamond Dichtol | - | Dichtol WFT standard #1532 | Leering
2 | 3.1 | Glue Loctite | - | Loctite super glue 4061 | Eriks
2 | 3.11 | Connector G3/8" - 22M | 1 | Custom design | Heemskerk
2 | 3.12 | Connector G1/2" - 22M | 2 | Custom design | Heemskerk
2 | 3.13 | Flow sensor | 1 | 0-100 L/min, 24V, max 6W See the Technical Manual (4.12) for detailed specifications | VPinstruments
2 | 3.14 | Mixing chamber | 1 | Custom design See the Technical Manual (4.4) for detailed specifications | RPP
2 | 3.15 | Proportional Inhalation Valve | 1 | Model: PCS-FV-010-EV-IV. Inlet pressure: 0.1-1 bar gauge. Outlet pressure: 0-0.15 bar gauge. Max operating pressure: 1 bar gauge. Orifice Size: 4,5 mm See the Technical Manual (4.7) for detailed specifications | Pressure control solutions
2 | 3.16 | Pressure regulator | 2 | DRV1340 Pressure regulator 4bar See the Technical Manual (4.2) for detailed specifications | Kramp
2 | 3.17 | FDM 3D prints | 1 | Printed with PLA (polylactic acid)
3 | 3.17.1 | Tube doublemount | 1 | Custom design: mount on bottom plate to fixate inspiratory and expiratory tubes and pressure tubes | MTB3D
3 | 3.17.2 | Flow sensor protection | 1 | Custom design: cap to protect flow sensor | MTB3D
3 | 3.17.3 | Pressure relief print | 1 | Custom design: plate to fixate pressure relief to bottom plate | MTB3D
3 | 3.17.4 | Elektronics cover | 1 | Custom design: housing for electronics | MTB3D
3 | 3.17.5 | Elektronics roof | 1 | Custom design: roof for electronics cover | MTB3D
3 | 3.17.6 | Speaker print | 1 | Custom design: housing for speaker | MTB3D
3 | 3.17.7 | Cover | 1 | Custom design: cover for front of the tube doublemount | MTB3D
3 | 3.17.8 | FlowsensorBasket | 1 | Custom design: fixation of flow sensor to bottom plate | MTB3D
2 | 3.18 | Ventilator | 1 | Noctua NF-A8 5V PWM USB 80mm Fan See the Technical Manual (4.20) for detailed specifications | Azerty
2 | 3.19 | NIST fitting O2 | 1 | Custom design See the Technical Manual (4.1) for detailed specifications | Heemskerk
2 | 3.2 | NIST fitting AIR | 2 | Custom design See the Technical Manual (4.1) for detailed specifications | Heemskerk
2 | 3.21 | 22mm-22mm connector | 2 | Intersurgical reference number: 1960000 See the Technical Manual (4.10) for detailed specifications | Merkala/Intersurgical
1 | 4 | Fasteners Mechanic - Housing | 1
2 | 4.1 | NIST air / NIST O2 | 1
3 | 4.1.1 | Bolt M3x12 | 6 | Steel
3 | 4.1.2 | Nut M3 | 6 | Steel
3 | 4.1.3 | Ring M3 | 6 | Steel
2 | 4.2 | MFC air / MFC O2 | 1
3 | 4.2.1 | Bolt M4x6 | 4 | Steel
3 | 4.2.2 | Ring M4 | 4 | Steel
2 | 4.3 | Mixing chamber | 1
3 | 4.3.1 | Bolt M5x10 | 3 | Steel
3 | 4.3.2 | Nut M5 | 3 | Steel
3 | 4.3.3 | Ring M5 | 3 | Steel
2 | 4.4 | Digital pressure regulator | 1
3 | 4.4.1 | Bolt M5x12 | 2 | Steel

3 | 4.4.2 | Ring M5 | 2 | Steel
3 | 4.4.3 | Laser cut plate for proportional inhalation valve | 1 | Custom design
2 | 4.5 | 3D printed components | 1
3 | 4.5.1 | Bolt M4x12 | 8 | Plastic
3 | 4.5.2 | Bolt M4x16 | 2 | Plastic
3 | 4.5.3 | Nut M4 | 14 | Plastic
3 | 4.5.4 | Ring M4 | 10 | Plastic
3 | 4.5.5 | M4x20 Countersunk screws | 4 | Plastic
2 | 4.6 | Solenoid Control Valve | 1
3 | 4.6.1 | Bolt M4x16 | 1 | Steel
3 | 4.6.2 | Ring M4 | 1 | Steel
2 | 4.7 | Speaker and electronics | 1
3 | 4.7.1 | M4x14mm Countersunk screws | 8 | Self tapping, steel
3 | 4.7.2 | Machine Screw M2.5x10 | 14 | DIN 7985, M2.5, 10 mm, Steel, Zinc, Recessed Pan Head Pozidriv
3 | 4.7.3 | Standoff M2.5x11 | 4 | Nickel Plated, Brass, M2.5, Hex Female, 11 mm, 11 mm
3 | 4.7.4 | Standoff M2.5x18 | 4 | Steel, M2.5, Hex Male-Female, 18 mm, 24 mm
3 | 4.7.5 | Standoff M2.5x30 | 3 | Steel, M2.5, Hex Female-Female, 30 mm
3 | 4.7.6 | Push-In Rivet | 6 | Black Nylon Fir Tree Push-In Rivet. Item code: 27MXT003006
3 | 4.7.7 | Screw M2.5x8 | 2 | DIN7500, M2.5, 8 mm, Zinc, Steel, Recessed Pan Head Pozidriv
3 | 4.7.8 | Tooth lock washer M4 | 7 | Steel
3 | 4.7.9 | Tooth lock washer M5 | 5 | Steel
3 | 4.7.10 | Ring Tongue terminal M4 | 3 | Ring Tongue terminal M4 2.5mm2
3 | 4.7.11 | Ring M2.5 | 7 | Steel
3 | 4.7.12 | Tooth lock washer M2.5 | 7 | Steel
2 | 4.8 | Top Cap | 1
3 | 4.8.1 | Push-In Rivet 1 | 6 | Black UL94 V-0 Nylon Round Snap Push-In Rivet, Item code: SRVO-4100B
1 | 5 | Manuals | 1
2 | 5.1 | Technical Manual | 1 | See 'Technical_Manual.pdf'
2 | 5.2 | Hand-out Instruction for User | 1
2 | 5.3 | Instructions for Use | 1 | See 'Instructions for Use.pdf'
1 | 6 | Packaging | 1
2 | 6.1 | Pallet and box | 1 | JOPAK
2 | 6.2 | Sticker | 1 | Stickerkoning

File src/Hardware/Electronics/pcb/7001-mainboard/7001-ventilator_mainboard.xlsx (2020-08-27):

Sync | Ref | Qty | Value | Footprint | MPN | Farnell | Mouser | Digikey
1 | R16, R17, R8, R9, | 4 | 0 | Resistor_SMD:R_0805_2012Metric |  | 2447574
1 | R5, R4, | 2 | 33R | Resistor_SMD:R_0805_2012Metric |  | 2447640
1 | R49, R50, R41, R42, R43, | 5 | 150 | Resistor_SMD:R_0805_2012Metric |  | 2747563
1 | R3, R12, R22, R24, R23, | 5 | 1k5 | Resistor_SMD:R_0805_2012Metric |  | 2447592
1 | R29, R40, R38, R19, R44, R37, R46, R45, | 8 | 3.3k | Resistor_SMD:R_0805_2012Metric |  | 2447651
1 | R34, R36, R32, R21, | 4 | 4.7k | Resistor_SMD:R_0805_2012Metric |  | 2447672
1 | R47, | 1 | 150 1% | Resistor_SMD:R_0805_2012Metric
1 | R48, | 1 | 2.32k 1% | Resistor_SMD:R_0805_2012Metric
 | ~~R48,~~ | ~~1~~ | ~~2.2k~~ | ~~Resistor_SMD:R_0805_2012Metric~~
1 | RV1, | 1 | Varistor | Jitter_Footprints:WE_VS_Varistor | 82551250
1 | R6, R35, R39, R15, R18, R11, | 6 | 10k | Resistor_SMD:R_0805_2012Metric |  | 2447553
1 | R31, R10, R1, R2, | 4 | 68k | Resistor_SMD:R_0805_2012Metric |  | 2447706
1 | R33, R14, R20, R13, | 4 | 100k | Resistor_SMD:R_0805_2012Metric |  | 2447551
1 | C10, C12, | 2 | 18pF | Capacitor_SMD:C_0805_2012Metric |  | 2821165
1 | C34, | 1 | 470pF | Capacitor_SMD:C_0805_2012Metric |  | 2409053
1 | C40, C20, C7, C35, C37, | 5 | 2.2nF | Capacitor_SMD:C_0805_2012Metric |  | 1414681
1 | C5, C6, C36, | 3 | 1nF | Capacitor_SMD:C_0805_2012Metric |  | 3013468
1 | C17, C45, C27, | 3 | 2.2nF 50V | Capacitor_SMD:C_0805_2012Metric |  | 1414681
1 | C46, C47, | 2 | 10nF 100V | Capacitor_SMD:C_1206_3216Metric | 885012208112
1 | C28, C29, C1, C23, C49, C2, C3, C21, C15, C50, C43, C8, C9, C31, C33, | 15 | 100nF | Capacitor_SMD:C_0805_2012Metric |  | 1650866
1 | C19, C39, C48, C51, C54, | 5 | 100nF 50V | Capacitor_SMD:C_0805_2012Metric |  | 1650866
1 | C11, C4, C52, C30, C32, | 5 | 1uF | Capacitor_SMD:C_0805_2012Metric |  | 2688485
1 | C13, | 1 | 4.7uF | Capacitor_SMD:C_0805_2012Metric |  | 2346968
1 | C25, C16, C53, | 3 | 10uF | Capacitor_SMD:C_0805_2012Metric |  | 3013485
1 | C38, C18, C42, C44, C41, C24, C14, C26, | 8 | 10uF 50V | Capacitor_SMD:C_1210_3225Metric |  | 2834943
1 | C22, | 1 | 330uF | Jitter_Footprints:CP_Elec_12.5_MAL214699107E3 | MAL214699107E3 | 2859824
1 | D1, D2, D11, | 3 | D_Schottky | Diode_SMD:D_SOD-123F | NRVTS245ESFT3G | 3003750
1 | D3, | 1 | S5MB R5G 100V | Diode_SMD:D_SMB | S5MB R5G
1 | D4, | 1 | D_TVS | Jitter_Footprints:WE-TVSP_TVS_DIODE | 824501301 | 2536572
1 | D7, D6, D5, D8, D9, | 5 | Green | LED_SMD:LED_0805_2012Metric | KP-2012LSGC | 2463991
1 | D10, | 1 | Red | LED_SMD:LED_0805_2012Metric | KPT-2012EC | 2099236
1 | FB1, FB2, | 2 | BLM18HE601SN1D | Inductor_SMD:L_0603_1608Metric | BLM18HE601SN1D | 2443238
1 | FL1, | 1 | 744282010 | Jitter_Footprints:L_CommonMode_Wuerth_WE-SCC | 744282010
1 | J1, | 1 | USB_B_Micro | Jitter_Footprints:USB_Micro-B_Molex_47346-0001 | 47346-0001 | 1568026
1 | J5, | 1 | 5-pin screw terminal vertical | Jitter_Footprints:TerminalBlock_Wurth_WR-TBL_691321100005_1x05_P3.50mm_Vertical | 691321100005
 | ~~J5,~~ | ~~1~~ | ~~2-pin screw terminal~~ | ~~Jitter_Footprints:TerminalBlock_Wurth_WR-TBL_691321100005_1x05_P3.50mm_Vertical~~ | ~~691321100005~~
 | ~~J5,~~ | ~~0~~ | ~~2-pin screw terminal~~ | ~~Jitter_Footprints:TerminalBlock_Wurth_WR-TBL_691322110008_1x08_P3.50mm_Horizontal~~ | ~~691322110008~~
1 | J13, J14, J4, J3, | 4 | 2-pin screw terminal | Jitter_Footprints:TerminalBlock_Wurth_WR-TBL_691322110002_1x02_P3.50mm_Horizontal | 691322110002 | 1841315
1 | J6, | 1 | 5V out | Connector_PinHeader_2.54mm:PinHeader_1x05_P2.54mm_Vertical
1 | J2, J7, | 2 | 6-pin FFC connector | Jitter_Footprints:Hirose_FH12-6S-0.5SH_1x06-1MP_P0.50mm_Horizontal | FH12-6S-0.5SH | 1324538
1 | J9, | 1 | Raspberry_Pi_2_3 | Jitter_Footprints:PinSocket_2x20_P2.54mm_Vertical_holes_SMD | REF-182665-01 | 2827937
1 | J10, | 1 | 6-pin header | Connector_PinHeader_2.54mm:PinHeader_1x06_P2.54mm_Vertical
1 | J11, J8, | 2 | 5-pin screw terminal | Jitter_Footprints:TerminalBlock_Wurth_WR-TBL_691322110005_1x05_P3.50mm_Horizontal | 691322110005 | 1841318
 | ~~J11, J8,~~ | ~~2~~ | ~~2-pin screw terminal~~ | ~~Jitter_Footprints:TerminalBlock_Wurth_WR-TBL_691322110005_1x05_P3.50mm_Horizontal~~ | ~~691322110005~~ | 1841318
1 | J15, | 1 | 2x10-pin header | Connector_PinHeader_2.54mm:PinHeader_2x10_P2.54mm_Vertical_SMD | 61032021121
1 | J16, | 1 | 10-pin SWD header | Jitter_Footprints:connector_jtag_10pin_shrouded | 20021521-00010T1LF
1 | Q1, | 1 | NX3020NAKV,115 | Package_TO_SOT_SMD:SOT-666 | NX3020NAKV,115 | 2311182
1 | U1, U8, | 2 | MPRLS0001PG0000SA | Jitter_Footprints:MPRLS0001PG0000SA | MPRLS0001PG0000SA |  |  | 480-7100-1-ND
1 | U2, | 1 | TPD2E2U06 | Package_TO_SOT_SMD:SOT-553 | TPD2E2U06DRLR | 3116500
1 | U3, | 1 | LPC11U37FBD48-401_ | Package_QFP:LQFP-48_7x7mm_P0.5mm | LPC11U37FBD48/401 | 2115662
1 | U4, | 1 | MCP1825S-3302E | Package_TO_SOT_SMD:SOT-223-3_TabPin2 | MCP1825S-3302E | 1578404
1 | U5, | 1 | S24SE05004PDFA_DC-DC | Jitter_Footprints:DCDC-5V_S24SE05004PDFA | S24SE05004PDFA |  | 108-S24SE05004PDFA
1 | U6, U15, | 2 | MCP4725 | Package_TO_SOT_SMD:SOT-23-6 | MCP4725A1T-E/CH | 2774927
1 | U9, | 1 | ABPDXXX000XXAX5 | Jitter_Footprints:ABPDXXX000XX0XX | ABPDANT015PGAA5
1 | U11, | 1 | MPVZ5010GW6U | Jitter_Footprints:MPVZ5010GW6U | MPVZ5010GW6U |  | 841-MPVZ5010GW6U | 568-13502-ND
1 | U13, U14, U7, | 3 | ITS4142NHUMA1 | Package_TO_SOT_SMD:SOT-223 | ITS4142NHUMA1 | 1440816
1 | U16, | 1 | LD1086DTTR | Jitter_Footprints:TO-252-2 | LD1086DTTR (adjustable)
1 | Y1, | 1 | 12MHz | Crystal:Crystal_SMD_3225-4Pin_3.2x2.5mm | 7M-12.000MEEQ-T | 2308719
 | Non-pcb parts
 | K3, K4, K13, K14 | 4 | 2 way straight | Mates with 691322110002 | 691361100002 |  |  | 732-2751-ND
 | K5, K11, K8 | 3 | 5 way straight |  | 691361100005 |  |  | 732-2754-ND
 | K9 | 1 | 20-pin tussenheader RPI | wordt tijdens assemblage tussen pcb en RPI geplaatst | REF-182683-02

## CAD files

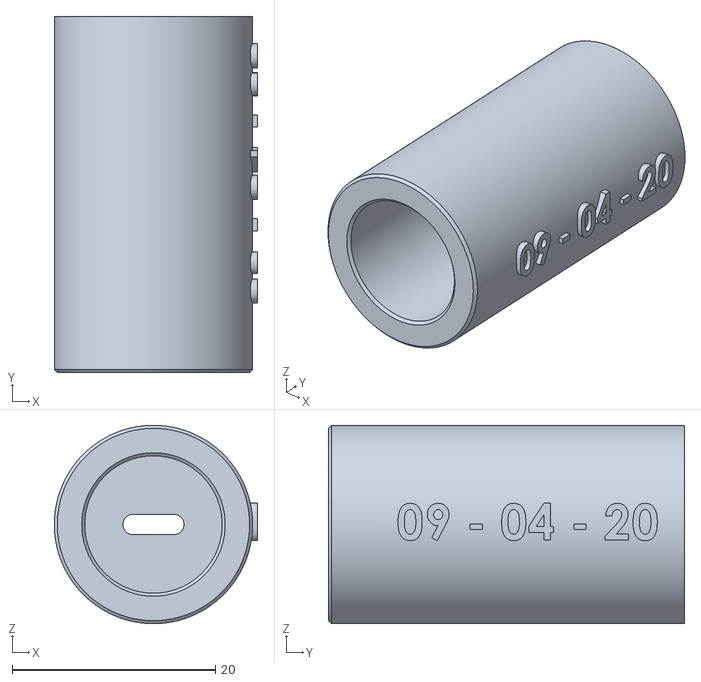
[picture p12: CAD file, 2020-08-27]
src/Hardware/3D-Print/FDM_Flow_Sensor_Cap.STL
20.0 x 35.0 x 19.5

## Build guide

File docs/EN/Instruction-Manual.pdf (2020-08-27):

# AIRone - Instructions For Use

OperationAIR

Version 1.5, April 22, 2020

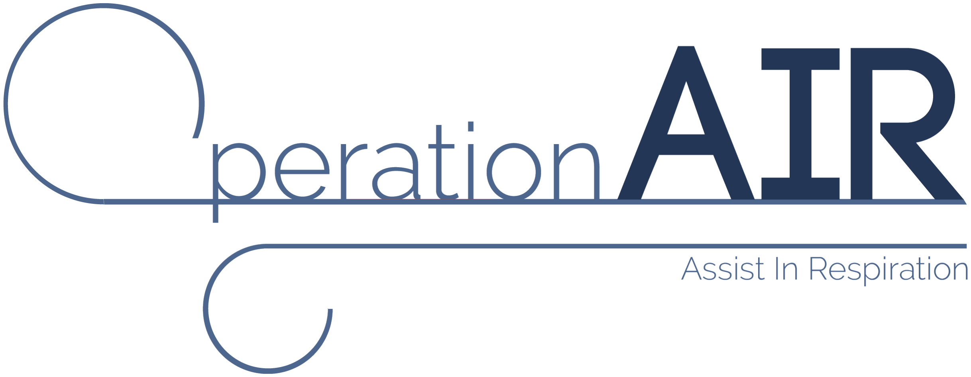
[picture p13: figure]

N! WARNING:

The device should only be
used by trained users and
these instructions should
be thoroughly read before
use.

Device version: 1.0
Firmware version: 1.0
Manual version: 1.5

Instructions For Use

## Liability and warranty

This medical device is being made available to healthcare institutions in the Netherlands which have explicitly requested this on the basis of the procedure established by the IGJ (https://www.igj.nl/actueel/nieuws/2020/03/23/coronavirus-meer-ruimte-voor-fabrikanten-en-leveranciers-bij-tekort-aan-medische-hulpmiddelen) (Inspection for Healthcare and Youth) to deliver non-CE-certified medical devices or devices which have not undergone the normal assessment procedure. Delivery of this medical device has happened on the request from the healthcare institution and the application of this medical device is based on the responsibility of the healthcare institution as defined in the ’Wet kwaliteit, klachten en geschillen zorg (Wkkgz)’. The manufacturer has reported the issue of this device to the IGJ conform aforementioned procedure.

## Customer support

If the product fails to function or when service, assistance or recalibration is needed, please contact:

OperationAIR
Mekelweg 2
2628 CD Delft
The Netherlands

Phone (service):
Phone (emergency):
Email:
Online:

06-53593426
06-53501569
service@operationair.org
operationair.org
©OperationAIR | Page 2 of 30

## Contents

1 Introduction | 5
1.1 Intended use | | 5
1.2 Intended user | | 5
1.3 Intended patient | | 5
1.4 Contra-indications | | 5
1.5 Side effects | | 5
2 Warnings | 6
3 Product description | 8
3.1 Product | | 8
3.2 Graphical User Interface | | 10
3.2.1 Tab general settings | | 12
3.2.2 Alarmsymbol | | 12
3.2.3 Tab alarmhistory | | 14
3.2.4 Tab patient data | | 14
3.2.5 Start/stop button | | 14
3.2.6 Settings for breathing frequency | | 14
3.2.7 Settings pressure | | 15
3.2.8 Settings FiO2 | | 15
4 Product specifications | 16
5 Installation | 18
5.1 Disposables | | 18
5.2 Breathing modes | | 18
5.3 Installation | | 18
5.4 Pre-use checks | | 19
6 Operation | 20
6.1 Set and start ventilation | | 20
6.2 Disconnection | | 21
6.2.1 Disconnection (Transfer to a conventional ventila-
tor) | | 21
6.2.2 Disconnection (patient died) | | 22
6.3 Settings | | 22

7 Alarms and notifications | 22
7.1 Notifications and symbols | | 23
8 Maintenance | 23
9 Cleaning and desinfection | 25
9.1 General | | 25
9.2 Cleaning | | 25
9.2.1 Instructions for cleaning | | 26
9.3 Desinfection | | 26
9.3.1 Instructions for desinfection | | 26
10 General safety instructions | 27
10.1 Symbols | | 28
11 Troubleshooting | 28
12 Classifications | 30
12.1 MDR classification | | 30

## 1 Introduction

The AIRone is an automatic ventilator for the treatment of patients in respiratory distress. The primary objectives of automatic ventilation are oxygenation, elimination of CO2 and taking over the breathing effort for the patient without continuous human intervention.

### 1.1 Intended use

The AIRone provides positive-pressure ventilation (PPV) for emergency automatic ventilation with adjustable positive end-expiratory pressure (PEEP), I:E ratio, peak pressure, oxygen concentration(%) and breathing frequency, created for the use on adult (suspected) COVID-19 patients who need non-weaned respiratory support to bridge a longer period of time until conventional ventilation becomes available.

### 1.2 Intended user

The AIRone should only be used by professional healthcare providers who are experienced in ventilation treatment, and have received training in the use of the AIRone ventilator.

### 1.3 Intended patient

The AIRone is intended to treat COVID-19 patients in acute respiratory distress, who are in need of mechanical ventilation. Patients should be intubated and kept in medically induced coma.

### 1.4 Contra-indications

- Pediatric patients

### 1.5 Side effects

The side effects that can occur when mechanically ventilating a patient are:

- Infection
- Irritation of the throat or lungs
- Vocal cord issues
- Lung injury

## 2 Warnings

N! The AIRone should ONLY be used when absolutely

needed and no conventional ventilation equipment is available.
N! The AIRone may only be used by trained users.

N! The AIRone is not able to preform assisted breath

initiated by a patient-trigger event, and should therefore ONLY be used to bridge the period from ICU intake until a conventional ventilation machine is available.
N! Always perform a Pre-use Check before connecting

the ventilator to a patient.
N! Do not use the device when it is visibly damaged.

N! Discontinue the device when the user-interface

shows unfamiliar warnings, when alarms cannot be resolved, or in the case of unfamiliar or unexpected behaviour.
N! When connected to a patient:
- Do not leave the patient unattended
- Continuously monitor the device and the patient
- Do not disconnect any hoses or connectors
N! Manual backup ventilation must be available at all

times.
N! Any serious adverse events must be reported to

service@operationAIR.org
N! Keep the system and its gas hoses clear of all

ignition sources.
N! Do not use the system with worn or frayed hoses

or hoses that have been contaminated by combustible materials such as grease or oil.

N! Oxygen-enriched gas is extremely flammable: if you

detect a burning odor, disconnect the oxygen supply to the ventilator and turn off the device.
N! The pressure sensor is (like most ventilator

machines) positioned at the device-end of the expiratory tube, due to a pressure decay over the inspiratory tube, the pressure delivered to the patient is 3-5 cmH2O lower than the value set on the Graphical User Interface (GUI).
N! When changing the FiO2, it will take some time

before the FiO2 in the inspiratory air will change. N! To avoid the risk of electric shock, the AIRone

must only be connected to a supply mains with protective earth.
N! Be careful with the alarm limit settings and do

not set the alarm limits at extreme values, this can render the alarm system useless.

## 3 Product description

### 3.1 Product

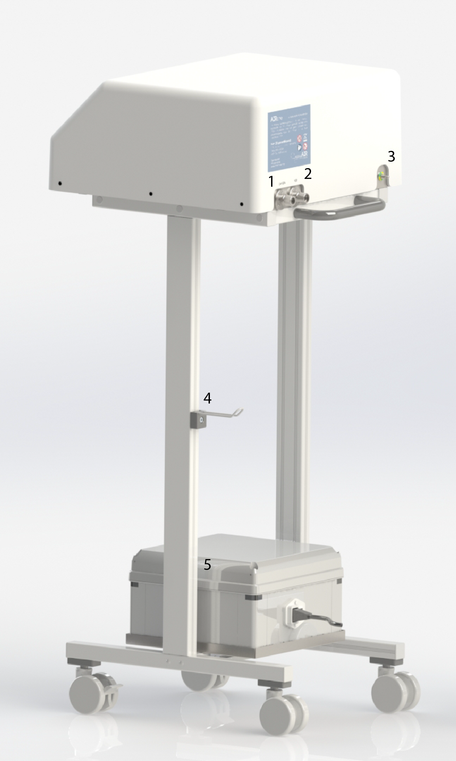
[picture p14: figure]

Figure 1: The frontview of the exterior of the AIRone. The numbers are explained below.

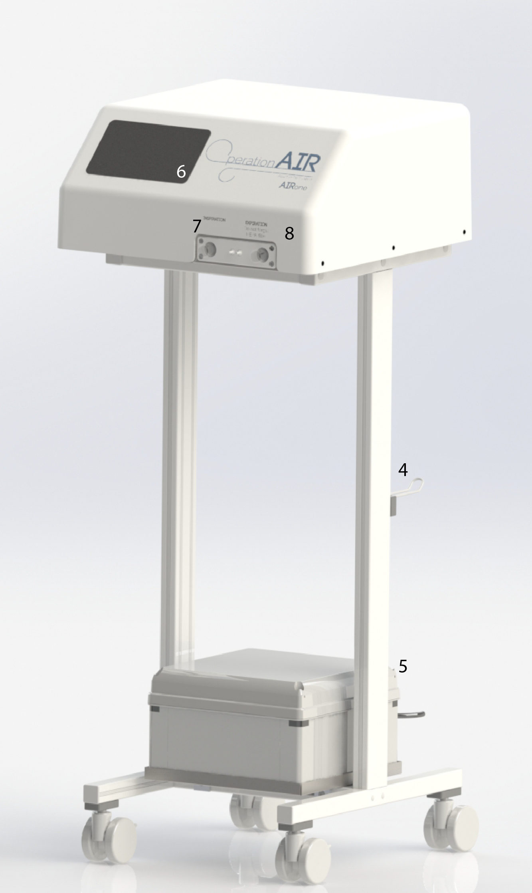
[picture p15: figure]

Figure 2: The backview of the exterior of the AIRone. The numbers are explained below.

1. Oxygen air input port
2. Compressed air input port

3. Additional grounding
4. Cable hook
5. Power supply unit
6. Graphical User Interface (GUI)
7. Patient-connection port (Inspiratory tube)
8. Patient-connection port (Expiratory tube)

### 3.2 Graphical User Interface

N! The user interface described in this section is

currently under construction and not definitive yet

The user interface consists of a touchscreen with multiple tabs. The main interface is shown below in figure 3 and 4. Different parameters and graphs are shown in this window.

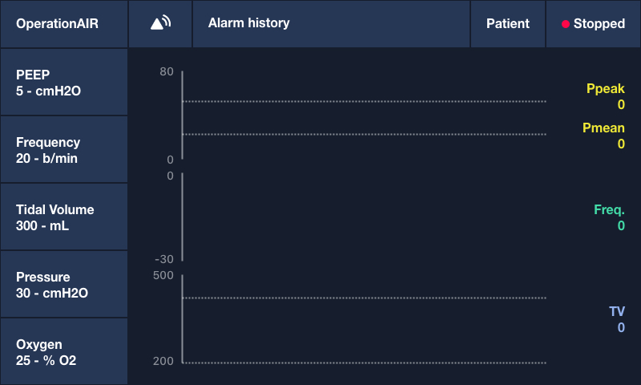
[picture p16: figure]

Figure 3: The main interface of the AIRone when not in ventilation mode.

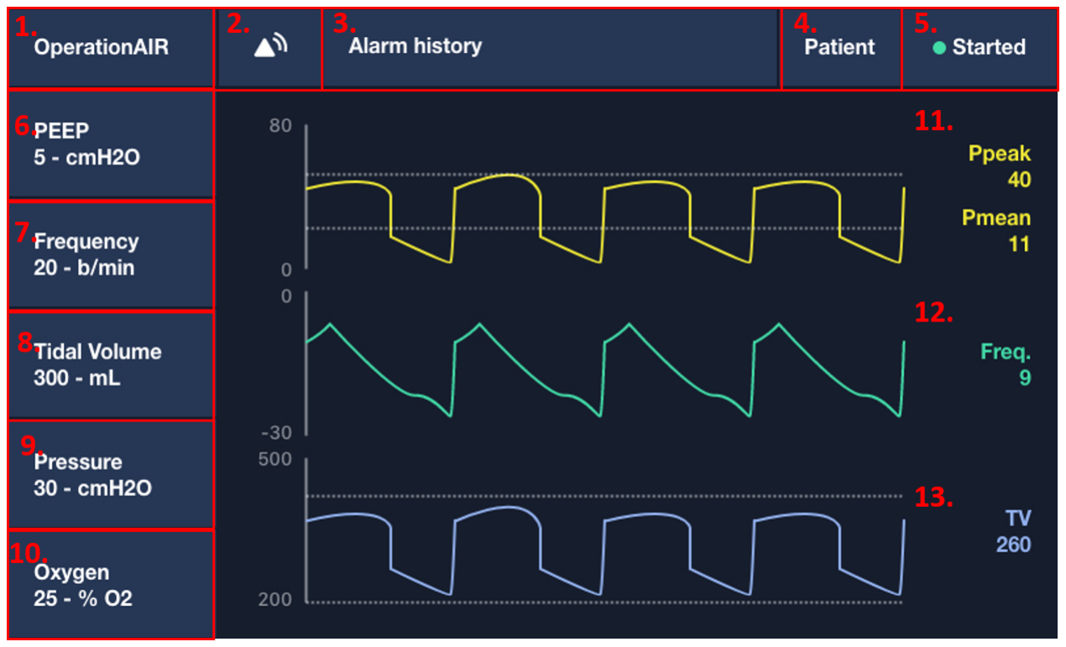
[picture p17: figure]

Figure 4: Het hoofdscherm van de gebruikersinterface tijdens beademing met de AIRone

The functionalities of the different tabs are numbered in figure 4 and will be explained in the subsections below.

1. Tab general settings
2. Alarm priority symbol
3. Tab alarm history
4. Patient data tab
5. Start/stop button
6. PEEP value
7. Settings for breathingfrequency
8. Tidal volume
9. Settings pressure
10. Settings FiO2
11. Flow graph
12. Druk graph

### 3.2.1 Tab general settings

In this tab, the brightness of the screen and the current time can be set. Also, the leak test, that needs to be executed before using the AIRone,is started in this tab.

### 3.2.2 Alarmsymbol

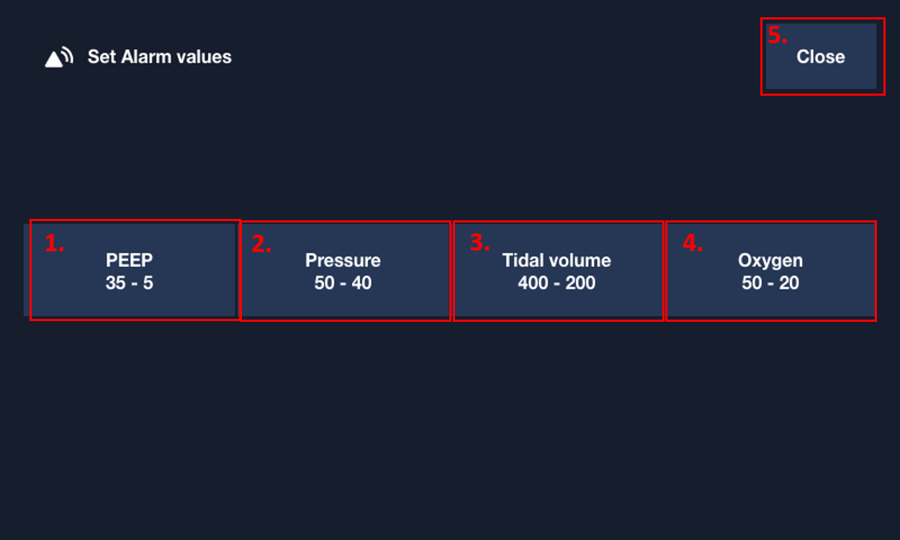
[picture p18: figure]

Figure 5: Tab with the different alarms in which the alarm limits can be set

1. Settings alarm limits PEEP
2. Settings alarm limits pressure
3. Settings alarm limits FiO2
4. Close this tab and return to the main interface

The interface for setting the alarm limits for PEEP is shown below in figure 6.

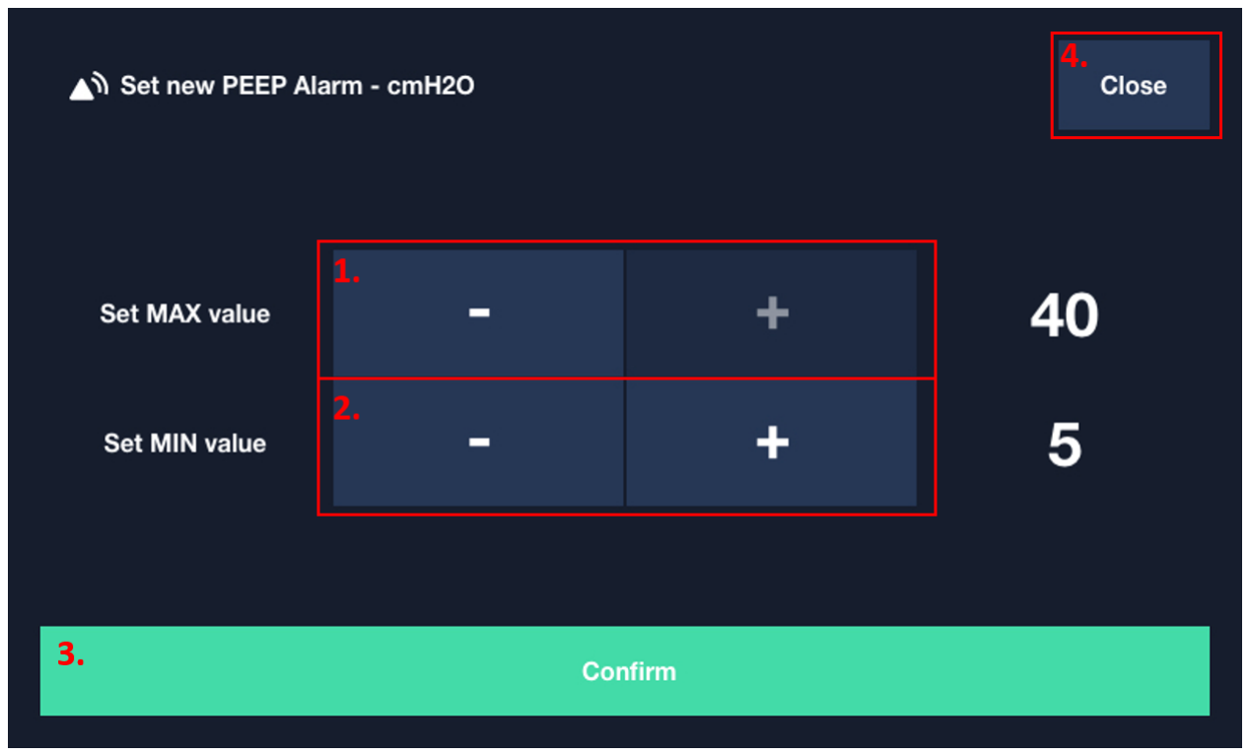
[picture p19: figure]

Figure 6: Tabblad PEEP instellingen.

In this tab, the limits can be set by pressing the plus or minus symbol.

1. Set the maximum PEEP value
2. Set the minimum PEEP value
3. Confirm the settings
4. Close this tab and return to the main interface

### 3.2.3 Tab alarmhistory

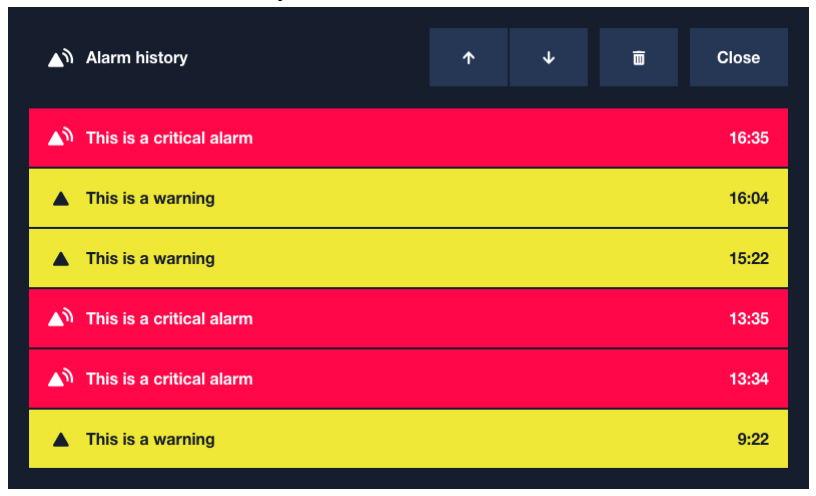
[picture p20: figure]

Figure 7: Example of the alarm history tab

### 3.2.4 Tab patient data

The patient data tab is shown below. In this tab, flow pressure and tidal volume curves of the past can be seen.

### 3.2.5 Start/stop button

The ventilation can be started and stopped with this button on the top right of the main interface.

in this tab. There are two variation of this tab. When the ventilation is stopped, figure ?? will appear with the option if you want to start the ventilation. When the ventilation is started, figure ?? will appear with the option to stop the ventilation.

### 3.2.6 Settings for breathing frequency

The breathing frequency and inspiratory expiratory ratio can be set in this tab.

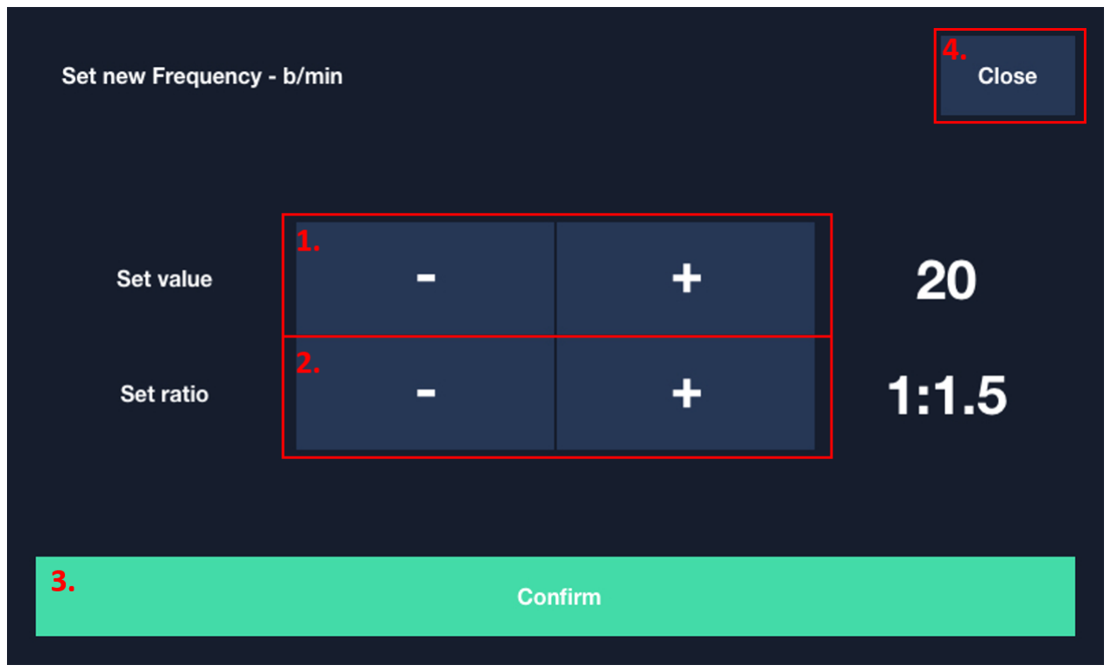
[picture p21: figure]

Figure 8: Tab breathingfrequency settings.

1. Set breathing frequency
2. Set the I:E ratio
3. Confirm these settings
4. To return to the main interface, press close.

### 3.2.7 Settings pressure 3.2.8 Settings FiO2

## 4 Product specifications

Productspecifications
Tidal volume | 5- 700 mL
Pressure above PEEP | 5-40 cmH2O
Positive end expiration pressure (PEEP) | 5-30 cmH2O
Maximum pressure | 70 cmH2O
Breathing-frequency | 5-40 b/min
Inspiration expiration ratio (I:E) | 1:1 - 1:3
Peak inspiration flow | 0-100 L/min
Pressure rise time, inspiration rise time | 0.3-0.7 sec
O2-concentration FiO2 | 21-100 %
Mass flow controllers | Accuracy: ± 1 % FSS Max output flow: 50 l/min
Displayed | flow and pressure
Weigth | 24.3 kilogram

Table 1: Productspecifications of the AIRone ventilator.

Electrical properties
Input voltage | 230-240 V AC
Input frequency | 50-60 Hz
Isolation | Class I
Compliance | IEC 60601-1-2
Battery duration | 30-45 minutes

Table 2: Electrical properties.

Operating conditions
Environment temperature | 15-25 degrees Celsius
Relative humidity | 10-90%
Atmospheric pressure | 0.995-1.05 bar

Table 3: Operating conditions.

## 5 Installation

### 5.1 Disposables

The disposables needed for full functionality of the AIRone that are not provided by OperationAIR are:

- The hoses with NIST connection for connecting the AIRone to the compressed air and oxygen infrastructure of the hospital should be in-house available.
- Heat and Moisture Exchanger (HME) filter
- High-efficiency particulate air (HEPA) filter
- Inspiratory and expiratory tubes for the connection of the AIRone to the patient
- Endotracheal tube

The intubation set, consisting of an endotracheal tube and the devices and anaesthetics needed to intubate the patient should also be in-house available.
The inspiratory and expiratory tubes connected to the HEPA and HME filter will later on be called "breathing circuit". Instructions for connection of these components is described below in the subsection set and start ventilation.

### 5.2 Breathing modes

Ventilation using the AIRone is pressure-controlled and forced. It is not possible to synchronise with spontaneous breathing of the patient. The start and end of the inspiration is determined by the AIRone, based on values specified by the user. Therefore, no spontaneous breathing tests are available and no back-up respiratory rate (i.e. a very low respiratory rate to allow intermittent spontaneous breathing) are possible.

### 5.3 Installation

1. Set the AIRone-ventilator in the desired position.
2. Use the brakes placed on the bottom of the trolley.
3. Connect the oxygen and compressed air hose to the AIRone via the NIST-connections.
4. Connect the oxygen and compressed air hose to the local gas network.

5. Connect the grounding cable
6. Connect the power supply cable to the main power supply.

### 5.4 Pre-use checks

N! The AIRone is not capable of self testing before

use
Before the patient is connected to the AIRone-ventilator, the following control tests need to be done.
Pre-use checks include tests and measurements of:
- Internal technical functionality
- Check if the AIRone is plugged

The internal technical functionality

1. Start the AIRone ventilator via the on/off-button at the power supply module.
2. Check if all parameters can be changed and if the alarms are working by changing the alarm limits
3. Check if the desired FiO2 can be reached.

## 6 Operation

The AIRone-ventilator must be installed as described in section 5: Installation. Before starting the procedure, check the unit, trolley, sensors, cables, connections and perform the pre-use checks described in subsection 5.4. Do not use a damaged device.

### 6.1 Set and start ventilation

N! Before preparing the patient for intubation,

be sure the AIRone ventilation system is working correctly by executing the pre-use checks.

1. Place the HEPA filter between the end of the expiratory tube and entry of the AIRone ventilator.
2. Attach the inspiratory and expiratory tubes to the AIRone-ventilator.
3. Place the HME filter at the end of the inspiratory tube.
4. Turn on the AIRone via the on/off-button at the power supply module.
5. Perform the pre-use checks
6. Select the desired ventilator settings using the touchscreen (see subsection 6.3).
7. Select the desired alarm limits using the touchscreen (see subsection 6.3).
8. Intubate patient and connect the endotracheal tube to the breathing circuit (inspiratory and expiratory tubes with the filters) following the in-house protocol.
9. Start ventilation by pressing start in the tab on the top right of the touchscreen.
10. Check if the HME-filter and the HEPA-filter are placed correctly.
11. Evaluate the flow- and pressure curves and observe the patient.
12. Evaluate the position of the endotracheal tube.
13. If necessary, optimise the ventilator settings based on patient observation and clinical parameters.

### 6.2 Disconnection

N! The device needs to be shut down before unplugging

the energy supply.
The AIRone needs to be disconnected from the patient if there is a conventional ventilation machine available, if the patient gets better and when the patient dies. The steps that need to be taken when disconnecting the AIRone from the patient are described below. The cleaning protocol for the AIRone-ventilator is described extensively in section 9.

### 6.2.1 Disconnection (Transfer to a conventional ventilator)

1. Prepare the conventional ventilator following the instructions of the ventilator.
2. Prepare patient for switching to a conventional ventilator according to the in-house protocol.
3. Disconnect the AIRone breathing circuit from the endotracheal tube.
4. Discart disposables with the medical waste following the in-house protocol.
5. Connect the endotracheal tube to the breathing circuit connected to the conventional ventilator and start ventilation.
6. Stop ventilation on the AIRone by pressing the "Stop"-button for 5 seconds.
7. Shut down the software by pressing the "shut down"-button in the "Menu" tab.
8. Turn the AIRone off via the on/off-button on the power supply module.
9. Disconnect the power supply cable
10. Disconnect the grounding cable
11. Disconnect the oxygen and compressed air hoses from the AIRone and local gas network
12. Clean AIRone-ventilator according to the instructions in section 9 of this manual.

### 6.2.2 Disconnection (patient died)

1. Disconnect the patient from the AIRone by disconnecting the breathing circuit and extubating the patient.
2. Discard the disposables with the medical waste following in-house protocol.
3. Stop ventilation by pressing the "Stop"-button for 5 seconds.
4. Shut down the software by pressing the "Shut down"-button in the "Menu"tab.
5. Turn AIRone off via the on/off-button on the power supply module.
6. Disconnect the power supply cable
7. Disconnect the grounding cable
8. Disconnect oxygen and compressed air hoses from AIRone and the local gas network.
9. Clean AIRone-ventilator according to the instructions in section 9 of this manual.

### 6.3 Settings

The following parameters can be set:

- PEEP [cmH2O]
- Breathing frequency [b/min]
- inspiratory, expiratory ratio [I:E ratio]
- FiO2

For further instructions on how to set these parameters, see subsection 3.2.

## 7 Alarms and notifications

The alarm limits can be set as described in subsection 3.2. There are multiple alarms, these can be turned of by the user. Alarms that went off are saved in the tab alarm history.
The AIRone has the following alarms:
- Low pressure

- High pressure
- Low FiO2 (≥ 5 min)
- High FiO2 (≥ 15 min)
- Low PEEP
- Small tidal volume
- Large tidal volume
- Uses battery power
- Battery running low

### 7.1 Notifications and symbols

The symbol that appears when an alarm is going off is shown below in figure 9.

Figure 9: Notification symbol of an alarm (IEC 60417-5308)

## 8 Maintenance

In this section the general guideline for maintenance is given. For the disposables that are not provided by OperationAIR, the guidelines of the manufacturer should be followed. To reassure the safety and reliability of the device, the user must follow the maintenance procedure.

N! Maintenance may only be executed by OperationAIR

certified maintenance personnel.
N! If the HEPA filter was not replaced in time or

not used during ventilation, call the OperationAIR maintenance servicecenter.
N! Before opening the AIRone for maintenance of the

interior, always be sure the AIRone is turned off and the power supply cable is unplugged.
Replacements inbetween patients
- HEPA filter
- HME filter

- Disposable tubes and hoses
- 3D-printed materials in the flowstream

Yearly maintenance

- General calibration
- General performance
Interval | Part | Procedure
Inbetween patients | Disposables | The disposable tubes, hoses, HEPA and HME filters need to be re- placed inbetween pa- tients
| Battery | Check if battery is fully charged, if not, charge the battery for at least four hours by connect- ing the AIRone to the main energy supply
| All 3D-printed material in the flowstream | All 3D-printed mate- rials in the flowstream should be inspected and replaced if neces- sary
Yearly | General calibration | Test using a test lung with sensors
| General performance

Table 4: Maintenance: overview of replacements.

The AIRone ventilator may not be disposed by the institution. When the AIRone is out of use or damaged, please contact service@operationair.org and follow further instructions.

## 9 Cleaning and desinfection

N! Do not use detergents containing abrasive

components when cleaning and desinfecting the AIRone. N! Do not use detergents with a chlorine concentration

higher than 10.000 ppm or 1%.
N! Do not use detergents containing acetone when

cleaning and desinfecting the touchscreen.
N! Do not use detergents containing alcohol at

temperature higher than 60 degrees Celsius when cleaning and desinfecting the AIRone.
N! Do not clean the inside of the AIRone. This could

damage to the internal components.
N! Follow the in-house protocol for cleaning and

desinfection of devices that have been in contact with COVID-19 patients.

### 9.1 General

For cleaning and disinfection, the in-house protocols for cleaning medical equipment must be followed. The power supply, gas supply hoses and disposable components must be disconnected from the AIRone before cleaning. Too much water around electrical connections should be avoided. Excess water should be removed so that no liquid penetrates into the material. During cleaning and disinfection, avoid contamination by changing cloths and gloves after cleaning dirty surfaces. Cleaning should be done from top to bottom, from the cleanest to the dirtiest part and with non sterile gloves.

### 9.2 Cleaning

All components of the AIRone should be cleaned after each use and if there is visible contamination. The cleaning should be done with an impregnated disposable cloth or a cleaning cloth with a soap solution consisting of warm water with medical soap or a mild detergent. Table 5 gives an overview of the parts to be cleaned.

### 9.2.1 Instructions for cleaning

1. Check if power supply, oxygen and compressed air hoses and disposables are disconnected. If not, disconnect them first.
2. Use an impregnated disposable disposable cloth or clean cloth with soap solution (mild all-purpose cleaner, medical soap, etc.).
3. Clean outside of AIRone, from ‘clean’ to ‘dirty’ and from the top down. Replace cleaning cloth or gloves in between if necessary.
4. Allow the surface to air dry or use a suitable drying cloth.
5. Inspect all components and replace or report if necessary.

### 9.3 Desinfection

Desinfection should be done in case of visible contamination with body fluids or isolation measures, according to the in-house protocol. Before desinfection is started, cleaning is required. Desinfection can be done with a medical desinfectant (chlorine 70 %, chlorine solutions 250-1000 ppm, etc.). Table 5 gives an overview of the components to be desinfected.

### 9.3.1 Instructions for desinfection

1. Check if power supply, oxygen and compressed air hoses and disposables are disconnected. If not, disconnect them first.
2. Before disinfection is started, clean the AIRone.
3. Moisture the surface with a medical desinfactant (alcohol 70 %, chlorine solution, etc.)
4. Allow the surface to air dry.
5. Inspect all components and replace or report if necessary.

Part | Frequenty | Cleaning | Disinfection
Exterior | Inbetween patients* | Yes | Yes
Inspiration and ex- pirationtubes | Follow in-house protocol | Yes | Yes
Oxygen | and | air
tubes | Follow in-house protocol | Yes | Yes
NIST connections | Inbetween patients* | Yes | Yes
Trolley | Inbetween patients* | Yes | Yes
Touchscreen | Inbetween patients* | Yes | Yes

Table 5: Overview components to be cleaned.

*Sooner if visibly contaminated.

## 10 General safety instructions

- No smoking near the AIRone ventilator.
- Prohibited to sit, stand on or lean against the ventilation machine.
- The AIRone ventilator is not intended to use during transport.
- The AIRone ventilator should be unplugged and switched off when damage is suspected. i.e. after a fall or when other parts are visibly damaged.
- Before use, verify correct connection of the grounding cable.
- The battery is intended for backup and not for primary energy supply.
- It is not advised to use the AIRone ventilator in pediatric patients.
- Use the breaks when the device is not being moved.

### 10.1 Symbols

Safety symbols and their explanation.

Figure 10: Read the instructions for use

Figure 11: Prohibited to throw away the AIRone ventilator. Contact OperationAIR for instructions on returning the AIRone.

Figure 12: incendiary

Figure 13: Do not stand, sit, lean on or push the AIRone.

## 11 Troubleshooting

N! Always check the entered limits of the alarms.

Alarm | Cause | Remedy
AIRone uses battery | The power cable is disconnected | Connect the AIRone to the main power supply
Battery almost empty | Battery used for too long | Connect the AIRone to the main power supply
Plateau pressure too high | Hardware or software problem | Switch patient to another ventila- tion machine and call the Opera- tionAIR service number
Low tidal volume | Hardware problem, | Switch patient to another ventila- tion machine and call the Opera- tionAIR service number

| Software problem, | Check the O2-saturation of the pa- tient. If sufficient, call the Opera- tionAIR service number. If insufficient, switch patient to another ventilation machine and then call the OperationAIR service number.
| Tube problem | Check the tubes for hitches
PEEP too high | Hardware problem, | Switch patient to another ventila- tion machine and call the Opera- tionAIR service number.
| Software problem, | Check the O2-saturation of the pa- tient. If sufficient, call the Opera- tionAIR service number. If insufficient, first switch patient to another ventilation machine and call then the OperationAIR service number.
| Tube problem | Check the tubes for hitches
Low | expiratory
minute volume | Hospital oxygen in- frastructure is insuf- ficient | Connect oxygen tanks and follow the in-house protocol
Low FiO2 (≥ 5 min) | Hardware problem, | Switch patient to another ventila- tion machine and then call the Op- erationAIR service number.
| Software problem, | Check the O2-saturation of the pa- tient. If sufficient, call the Opera- tionAIR service number. If insufficient, first switch patient to another ventilation machine and then call the OperationAIR service number.
Low plateau pressure | Hardware problem | Switch patient to another ventila- tion machine and call the Opera- tionAIR service number.
Low PEEP | Hardware problem | Switch patient to another ventila- tion machine and call the Opera- tionAIR service number
High FiO2 (≥ 15 min) | Hardware problem, | Switch patient to another ventila- tion machine and call the Opera- tionAIR service number.

Software problem, | Check the O2-saturation of the
patient. If sufficient, call maintenance.
If insufficient, switch patient to another ventilation machine and call the OperationAIR service number.

## 12 Classifications

### 12.1 MDR classification

Classification to 2017/745 | Class IIb
Directives | Medical Device Directive 2017/745 annex VIII.

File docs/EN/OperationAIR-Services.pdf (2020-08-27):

# SERVICE STRUCTURE

In this document you will find an overview of included services that are offered to hospitals, aiming to optimize the use of the AIRone ventilator. The service accompanying the AIRone is provided by a service team of OperationAIR. Summarized, the service will consist of the following activities and means:

Instruction day
With the implementation of the AIRone ventilator an instruction day is offered, on which two team members will be visiting the hospital and stay stand-by for the duration of six hours. The instruction day will (depending on ICU requests) consist of:
- Training of key-users,
- Installation support of AIRone ventilators,
- Maintenance instructions to medical technology staff of the ICU department and,
- Explanation of service structure.

Documentation
All (key) users will be provided with documentation, including (technical) manuals, training documents and maintenance instructions. These documents will also be made available through online platforms.

Service desk
Questions and/or remarks can be communicated to the service team through the email-address or regular phone number. In case of emergency, hospitals can contact the service team through the emergency phone number which is 24/7 available.

These services consist of training, support and maintenance. This is further elucidated in the following sections.

## Training

To optimize training of professionals and ensure safe use of the AIRone ventilator, a training plan has been developed in cooperation with a medical-educational specialist. The trainings consists of a combination of training-, communication- and support structures.

The service team will hold responsibility for training key-users (as defined by the hospital department, often medical ventilation experts). The hospital/department (ICU) will hold responsibility of other users and registration of trained professionals. The training of other users will be supported by the provided training material. The service team can be contacted either though telephone or e-mail for questions or remarks.

Key-user training (train-the-trainer)
To get familiar with the use of the AIRone ventilator, key-users will be given an explanation of the basic principles and will be given instructions on how to use the ventilator. The key-users and staff required to follow the training are defined by the hospital department. To ensure efficiency, a minimum of two key-users have to be present at the training. The training will take approximately 20 minutes, in which the training layout can be adjusted based on availability staff receiving training.

Other users
Key-users that have followed the training(trainers) will be training other users. It is the responsibility of the head of department/teammanager to ensure every user of the AIRone ventilator is trained in using the device. Healthcare professionals that have received training from a key-user/trainer will be registered by means of a list that is present on the department. This is meant to provide a clear overview of all personnel that is training in using the ventilator.

OperationAIR teachers
Service team members of OperationAIR that train key-users, are provided with an extensive (technical) manual. Also, a general meeting is held (in line with local guidelines on disease control), in which didactic skills, responsibilities, use of the device, and possible issues and questions are discussed. Only team members that have attended this meeting and that have read the extensive manual will be giving training to key-users.

Instruction day support
During the instruction day, team members of OperationAIR will be present on-site to provide support in installation of the AIRone ventilator and to answer questions. If possible, these team members can provide additional training to other users.

Training material
Training material will be available in the form of:
- Powerpoint presentation: Train-the-trainer
Key-users will be trained in using the AIRone ventilator with a presentation. The slides will be shared, so key-users and other uses can consult them retrospectively.
- LearningSpace
An online performance-support platform is available containing all necessary information regarding safe use of the AIRone ventilator. This learning space can also be consulted outside of the hospital.
In this learning space a description is given for different processes: installation, set-up, control and disconnection. Also, the more complex actions will be further explained. Finally, the learning space contains an FAQ-list containing answers and solutions to frequently asked questions. The learning space will be continuously updated based on practical experiences.
- User manual
An extensive user manual will be offered to the department and is also available through the learning space.
- Hand-out manual
A short, visually attractive summary will be offered, which can be placed in patient rooms or break rooms. Through this hand-out, users can get a quick recap on safely using the AIRone ventilator. On this hand-out, the emergency phone number will also be provided, as well as an overview of alarms and a QR-code to the Learning space.

# Maintenance and support

During the instruction day, the medical technology manager of the department (ICU) will be given an introduction to the AIRone ventilator and an explanation about possible maintenance that has to be performed on the device. Also, he/she will be given the technical manual, containing all relevant technical details with extensive descriptions.
In the case of technical issues in using the AIRone ventilator, the service team can be contacted through the following channels:

The emergency telephone is available 24/7 and will be held by team members of the service team with in-depth knowledge of the technical design of the AIRone ventilator. They will be able to directly advise the user. In the case of insufficient ability to give advice through the phone, a service team member will be coming to the hospital as soon as possible to provide on-site support in solving technical issues.

In cases that do not require direct technical support (non-emergency), the service team can be contacted to the regular phone number or the e-mail address. Both will be managed by team members with in-depth knowledge of the technical design of the AIRone ventilator. The user will receive support through the phone. If necessary, a team member will be coming to the hospital to provide on-site support. This phone number and e-mail address can also be used for other questions and/or technical issues.

All technical issues emerging from using the AIRone ventilator will be strictly monitored and evaluated. In this way, often occurring issues can be detected and solutions can be found.

Post-market surveillance will be performed. Several days after introduction of the AIRone ventilator in a hospital, the team will actively contact the users to evaluate the use of the device and answer questions. In this way, input can be collected for further development of the AIRone ventilator.

Emergency

Non-emergency

Contact emergency phone number 24/7 available

Contact regular phone number or email 9:00-17:00h available

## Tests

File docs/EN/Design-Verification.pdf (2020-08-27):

| Design Verification
OPERATIONAIR: OperationAIR (OperationAIR) | Date: 2020/04/29 14:28:42
Document: 4.1 | Page: 1 / 75

All dates and times are in the project’s default time zone and formatting.

### INTRODUCTION

This document provides a summary of the design verification activities and results for the AIRone emergency ventilator. This includes verifiation of design specifications, safety tests, and usability tests.
The design specifications are described in detail in the Design Specifications Document. For each specification, the applicable test reports are summarized in this document.
Usability tests and safety tests are also summarized in this document.

### TABLE OF CONTENTS

### CONCLUSION

The AIRone is currently undergoing the final stages of design verification. Almost all design specifications have been verified. Usability testing has yielded some improvements to the design, which have all been implemented and verified as well. Electrical safety has been verified. Although full compliance with the standards regarding Electromagnetic compatibility has not been acquired, we believe that the AIRone is ready for clinical testing when needed in emergency situations where no conventional ventilation equipment is available.

(OperationAIR) | Date: 2020/04/29 14:28:42
Document: 4.1 | Page: 2 / 75

### USABILITY TESTS

Two formative usability test sessions were held with several intensive care physicians and ventilation specialists. Special focus was paid to ease of use, safety, and applicability for COVID-19 patients on intensive care units in The Netherlands.

03-04-2020
Participants:
, Intensivist; | , Intensivist; | , Technical Physician; | , Technical Physician
Conclusion:
The device is intuitive to use. The current alarms are sufficient, but the default alarm limits should be smaller. COVID-19 patients generally require complex ventilation strategies, so the device must be able to handle high breathing rates up to 40/min with large minute volumes. Additionally, the possibility to perform expiratory holds is a must. Also a way to detect AutoPEEP should be added.

10-04-2020
Participants:
, Intensivist; | , Technical Physician; | , Ventilation Practicioner
Conclusion:
The user interface works as it should, comparable to standard ventilators. Starting ventilation is easy. The device is able to provide the ventilation performance that is required. Peak pressure is generally set as relative pressure above PEEP instead of relative to ambient pressure. Pressure settings and especially PEEP should be adjustable in small intervals of 1 or 2 cmH2O. The time-axis of the flow and pressure curves should be smaller, generally 4 to 5 breaths should be displayed.

### SAFETY TESTS

ELECTRICAL SAFETY
Leakage current testing was performed using the acceptance criteria for leakage current as defined in IEC 60601-1:2006. Measured leakage current was within acceptable limits for all tests.

ELECTROMAGNETIC COMPATIBILITY
Explorative tests were performed for radiated immunity, radiated emission, and electrostatic discharge. Tests and acceptance criteria were based on IEC 60601-1-2:2015.
Radiated immunity testing indicated that some components were sensitive for certain irradiated freqencies. The speaker emitted noise when irradiated at 54, 117 and 124 MHz. The UPS module started vibrating when

(OperationAIR) | Date: 2020/04/29 14:28:42
Document: 4.1 | Page: 3 / 75

irradiated with frequencies around 270 MHz. And the screen malfunctioned when irradiated in the 200 - 235 MHz range. The following design changes were made to eliminate these sensitivities:
- The speaker cable was placed directly on the protective earthing and capacitively coupled using conductive material
- Ferrite filters were placed on the cables to and from the UPS module
- The cable to the screen was shielded using conductive material and this shielding was connected to the protective earthing
- The screen was directly connected to the protective earthing
Radiated emission between 30 MHz and 1 GHz was measured in an anechoic chamber. Quasi-Peak emission limits were exceeded in two frequency bands: 42.7 dBμV/m around 40 MHz, and 51.9 dBμV/m at 219 MHz. Although these results technically constitute a failure, we consider the device acceptable for emergency use. Continued development is required.
Testing for bursts of electrostatic discharges at 8 kV showed that the flowsensor was susceptible. Discharges to the screws on the front of the device, close to the location of the flowsensor, could disrupt the sensordata communication. For this reason, the screws close to the flowsensor that were accessible from the exterior were replaced with non-conductive screws.

### DESIGN SPECIFICATIONS

Item | Tested By | Execution Date | Last Modification | Test Result
SPEC-31 Ventilation mode | XTC-30 Error margins: Pressure loss (TC-76) | 2020/04/02 | 2020/04/02 08:21:46 | passed
| XTC-49 Pressure Rise Time (TC-120) | 2020/04/05 | 2020/04/05 13:14:49 | failed
| XTC-38 Peak-plateau difference (TC-121) | 2020/04/02 | 2020/04/02 16:57:29 | passed
SPEC-46 Usability user-interface | XTC-110 Usability test (TC-65) | 2020/04/10 | 2020/04/24 09:47:51 | documentation
SPEC-34 Visualized measurements | XTC-2 Visualized measurements (TC-31) | 2020/03/27 | 2020/03/27 17:41:48 | passed
SPEC-150 Instructions For Use | XTC-127 IFU packed with device (TC-162) | 2020/04/24 | 2020/04/24 10:41:32 | passed
SPEC-42 Compatibility with standard hospital equipment | XTC-77 Compatibility with standard hospital equipment (TC-39) | 2020/04/06 | 2020/04/06 18:59:48 | passed
SPEC-141 Inspiratory hold | XTC-65 Inspiratory Hold (TC-156) | 2020/04/10 | 2020/04/10 07:45:23 | passed with deviation

(OperationAIR) | Date: 2020/04/29 14:28:42
Document: 4.1 | Page: 4 / 75
Item | Tested By | Execution Date

Last
Modification

Test Result

SPEC-156 Expiratory Hold | XTC-111 Expiratory Hold (TC-170) | 2020/04/24 | 2020/04/24 08:03:36 | passed
SPEC-73 Interruption of power supply | XTC-82 Back up battery (TC-10) | 2020/04/07 | 2020/04/10 08:03:11 | passed
SPEC-60 Breaks | XTC-66 IFU: Use breaks when needed (TC-104) | 2020/04/06 | 2020/04/06 10:01:15 | passed
| XTC-51 Breaks (TC-103) | 2020/04/05 | 2020/04/06 17:17:52 | passed
SPEC-27 Flow Sensor | XTC-56 Flow sensor (TC-24) | 2020/04/05 | 2020/04/05 11:57:41 | passed
SPEC-153 HEPA filter | XTC-112 HEPA filter (TC-171) | 2020/04/24 | 2020/04/24 08:11:37 | passed
SPEC-25 HME-filter | XTC-14 HME filter (TC-70) | 2020/03/31 | 2020/03/31 17:15:06 | passed
SPEC-166 Ventilator | XTC-123 Ventilator (TC-172) | 2020/04/24 | 2020/04/24 10:00:19 | passed
SPEC-155 Ppeak setting | XTC-109 Pressure setting (TC-168) | 2020/04/23 | 2020/04/23 09:42:42 | passed
SPEC-35 PEEP setting | XTC-43 PEEP value (TC-30) | 2020/04/06 | 2020/04/06 13:40:19 | passed
| XTC-46 PEEP stability (TC-133) | 2020/04/06 | 2020/04/06 14:09:20 | passed
| XTC-60 PEEP settings (TC-32) | 2020/04/05 | 2020/04/05 13:18:51 | passed
SPEC-20 Breathing rate setting | XTC-25 Error margins: Breating rate (TC-78) | 2020/04/06 | 2020/04/06 13:25:22 | passed
SPEC-38 I:E ratio setting | XTC-27 Error Margins: I:E ratio (TC-80) | 2020/04/02 | 2020/04/24 08:22:50 | failed
| XTC-69 I:E ratio (TC-148) | 2020/04/24 | 2020/04/24 08:13:07 | passed
SPEC-37 FiO2 setting | XTC-57 Fi02 setting (TC-34) | 2020/04/05 | 2020/04/05 12:01:25 | passed
SPEC-6 Alarm for Inspiratory O2 concentration (FiO2) | XTC-86 Oxygen alarm (TC-9) | 2020/04/07 | 2020/04/07 09:09:38 | passed
| XTC-87 Air pressure drop alarm (TC-155) | 2020/04/07 | 2020/04/07 09:19:03 | passed

(OperationAIR) | Date: 2020/04/29 14:28:42
Document: 4.1 | Page: 5 / 75
Item | Tested By | Execution Date | Last Modification | Test Result
SPEC-9 Alarm for positive end-expiratory pressure (PEEP) | XTC-101 PEEP alarm (TC-8) | 2020/04/13 | 2020/04/13 09:12:01 | passed
SPEC-8 Alarm for Tidal volume (Tv) | XTC-124 Tidal volume alarm I (TC-7) | 2020/04/24 | 2020/04/24 10:18:02 | passed
| XTC-125 Tidal volume alarm II (TC-68) | 2020/04/24 | 2020/04/24 10:19:26 | passed
SPEC-89 Alarm for Peak Pressure (Ppeak) | XTC-102 Plateau pressure alarm II (TC-83) | 2020/04/13 | 2020/04/13 09:19:16 | passed
SPEC-87 Alarm for Apnea or disconnect | XTC-103 Apnea/Disconnect alarm (TC-101) | 2020/04/13 | 2020/04/13 09:33:34 | passed
SPEC-84 Alarm for empty battery | XTC-128 Back-up battery empty alarm (TC-84) | 2020/04/24 | 2020/04/24 10:57:08 | failed
SPEC-19 Clear explanation per alarm on GUI | XTC-113 Clear explanation per alarm (TC-17) | 2020/04/24 | 2020/04/24 08:59:03 | passed
SPEC-95 Error margins: Tidal Volume | XTC-28 Error margins: Tidal Volume (TC-81) | 2020/04/02 | 2020/04/06 20:13:57 | passed with deviation
SPEC-94 Error margins: I:E ratio | XTC-27 Error Margins: I:E ratio (TC-80) | 2020/04/02 | 2020/04/24 08:22:50 | failed
SPEC-93 Error margins: FiO2 | XTC-26 Error margins: FiO2 (TC-79) | 2020/04/02 | 2020/04/02 09:32:59 | passed
SPEC-92 Error margins: breating rate | XTC-25 Error margins: Breating rate (TC-78) | 2020/04/06 | 2020/04/06 13:25:22 | passed
SPEC-90 Error margins: Lung/airway pressure | XTC-30 Error margins: Pressure loss (TC-76) | 2020/04/02 | 2020/04/02 08:21:46 | passed
SPEC-36 FiO2 range | XTC-26 Error margins: FiO2 (TC-79) | 2020/04/02 | 2020/04/02 09:32:59 | passed
SPEC-26 Tidal Volume | XTC-34 Tidal volume range (TC-23) | 2020/04/02 | 2020/04/02 09:19:27 | passed
SPEC-40 Inspiratory Flow | XTC-70 Inspiratory flow (TC-37) | 2020/04/06 | 2020/04/07 11:44:59 | passed
SPEC-118 Reliability | XTC-130 Measurement Reliability (TC-106) | 2020/04/24 | 2020/04/24 11:09:06 | passed
SPEC-128 14 day reliability | XTC-79 Long-term reliabillity (TC-38) | 2020/04/06 | 2020/04/08 11:01:57 | passed
| XTC-81 Specification of expected durability (TC-130) | 2020/04/07 | 2020/04/07 08:07:49 | passed with deviation

(OperationAIR) | Date: 2020/04/29 14:28:42
Document: 4.1 | Page: 6 / 75
Item | Tested By | Execution Date

Last
Modification

Test Result

SPEC-29 Peak pressure | XTC-106 Fail-safe valve (TC-67) | 2020/04/10 | 2020/04/15 11:22:04 | passed
SPEC-146 Flow sensor shielding | XTC-131 Flow Sensor (TC-169) | 2020/04/24 | 2020/04/24 11:10:20 | passed
SPEC-144 Airflow materials | XTC-114 Airflow materials (TC-159) | 2020/04/24 | 2020/04/24 09:01:40 | passed
SPEC-129 Robustness | XTC-91 Push test (TC-61) | 2020/04/08 | 2020/04/08 09:38:51 | passed
| XTC-92 Impact test (TC-62) | 2020/04/08 | 2020/04/08 09:39:39 | passed
| XTC-120 Internal components tightly attached (TC-4) | 2020/04/24 | 2020/04/24 09:46:59 | passed with deviation
| XTC-68 Tipping test (TC-109) | 2020/04/06 | 2020/04/06 11:15:24 | passed
| XTC-118 Tipping test II (TC-110) | 2020/04/24 | 2020/04/24 09:38:40 | passed with deviation
| XTC-11 Do not push warning (TC-129) | 2020/03/31 | 2020/03/31 15:58:06 | passed
SPEC-126 Cleaning and disinfection | XTC-115 Cleaning and disinfection (TC-127) | 2020/04/24 | 2020/04/24 11:12:51 | passed
SPEC-120 Alarms are easy to understand and intuitive | XTC-97 Alarms easy to understand (TC-119) | 2020/04/08 | 2020/04/08 11:56:22 | passed
SPEC-113 Impairment of cooling | XTC-94 Impariment of cooling (TC-99) | 2020/04/06 | 2020/04/08 11:18:41 | passed
SPEC-103 No air leakage | XTC-116 Pressure Hold (TC-91) | 2020/04/24 | 2020/04/24 09:20:20 | failed
SPEC-100 External exhaust outlets | XTC-58 External exhaust outlet oxygen rich environment (TC-86) | 2020/04/05 | 2020/04/05 12:13:52 | passed
SPEC-99 Temperature of inspirated air | XTC-93 Temperature of applied parts (TC-85) | 2020/04/08 | 2020/04/08 11:05:25 | passed
SPEC-85 High Voltage circuit outside casing | XTC-9 230 V circuit outside casing (TC-112) | 2020/03/30 | 2020/03/30 11:14:35 | passed
SPEC-83 Testing of the fail-safe valve during production | XTC-134 Fail safe valve test during production (TC-111) | 2020/04/28 | 2020/04/29 07:11:46 | passed

(OperationAIR) | Date: 2020/04/29 14:28:42
Document: 4.1 | Page: 7 / 75
Item | Tested By | Execution Date | Last Modification | Test Result
SPEC-80 Housing impact test | XTC-92 Impact test (TC-62) | 2020/04/08 | 2020/04/08 09:39:39 | passed
SPEC-79 Housing mechanical resistance | XTC-91 Push test (TC-61) | 2020/04/08 | 2020/04/08 09:38:51 | passed
SPEC-72 Leakage current testing | XTC-63 Leakage current testing (TC-54) | 2020/04/10 | 2020/04/10 08:02:28 | passed
SPEC-71 Patient leakage current | XTC-63 Leakage current testing (TC-54) | 2020/04/10 | 2020/04/10 08:02:28 | passed
SPEC-70 Touch current | XTC-63 Leakage current testing (TC-54) | 2020/04/10 | 2020/04/10 08:02:28 | passed
SPEC-67 Acoustic Energy | XTC-19 Sound test (TC-49) | 2020/04/06 | 2020/04/06 20:18:18 | passed
SPEC-65 Sharp edges | XTC-117 Sharp edges (TC-48) | 2020/04/24 | 2020/04/24 09:36:21 | passed
SPEC-63 Instability unintended force | XTC-118 Tipping test II (TC-110) | 2020/04/24 | 2020/04/24 09:38:40 | passed with deviation
SPEC-62 Instability incline surface | XTC-68 Tipping test (TC-109) | 2020/04/06 | 2020/04/06 11:15:24 | passed
SPEC-143 Visibility User Interface | XTC-119 Usability with protective equipment (TC-41) | 2020/04/24 | 2020/04/24 09:40:03 | passed
SPEC-145 Watchdog program | not covered by selected test run(s)
SPEC-53 Power Supply | XTC-74 Power supply (TC-47) | 2020/04/06 | 2020/04/06 17:30:32 | passed
SPEC-32 Expirated air | XTC-50 Expirated air (TC-29) | 2020/04/05 | 2020/04/05 07:26:32 | passed
SPEC-44 Non-conductive exterior casing | XTC-52 Non-conductive exterior casing (TC-74) | 2020/04/05 | 2020/04/05 08:05:32 | passed
SPEC-45 Protective equipment | XTC-119 Usability with protective equipment (TC-41) | 2020/04/24 | 2020/04/24 09:40:03 | passed
SPEC-23 Protected off switch | XTC-99 Off switch protection (TC-21) | 2020/04/09 | 2020/04/09 18:08:37 | passed
SPEC-22 The O2 and air input connectors | XTC-85 O2 and air input connectors (TC-20) | 2020/04/07 | 2020/04/07 09:05:22 | passed
SPEC-18 Battery use warning | XTC-129 Back up battery warning (TC-69) | 2020/04/24 | 2020/04/24 11:07:59 | failed

(OperationAIR) | Date: 2020/04/29 14:28:42
Document: 4.1 | Page: 8 / 75
Item | Tested By | Execution Date | Last Modification | Test Result
SPEC-5 Pressure relief valve | XTC-106 Fail-safe valve (TC-67) | 2020/04/10 | 2020/04/15 11:22:04 | passed
SPEC-4 Calibrate sensors during assembly | XTC-18 Calibrate sensors during assembly (TC-66) | 2020/04/01 | 2020/04/01 14:20:00 | passed with deviation
SPEC-2 Robustness internal components | XTC-120 Internal components tightly attached (TC-4) | 2020/04/24 | 2020/04/24 09:46:59 | passed with deviation
SPEC-1 Ingress of water | XTC-98 Splash proof (TC-3) | 2020/04/09 | 2020/04/09 18:06:49 | passed
SPEC-162 Installation Verification | XTC-132 Installation Verification (TC-174) | 2020/04/24 | 2020/04/25 10:37:38 | passed
SPEC-152 IFU: regulatory requirements | XTC-135 IFU: regulatory requirements (TC-165) | 2020/04/29 | 2020/04/29 09:45:44 | passed with deviation
SPEC-47 IFU: intended use | XTC-35 Clear explanation for intended use in IFU (TC-134) | 2020/04/02 | 2020/04/02 09:17:10 | passed
SPEC-13 IFU: Device not for use during transport | XTC-32 IFU: Not for use during transport (TC-12) | 2020/04/02 | 2020/04/02 08:58:38 | passed
SPEC-14 IFU: Check device before use | XTC-33 IFU: Check device before use (TC-13) | 2020/04/02 | 2020/04/02 09:03:16 | passed
SPEC-98 IFU: Do not use when damaged | XTC-31 IFU: Unplug device when damaged (TC-114) | 2020/04/02 | 2020/04/02 09:00:06 | passed
SPEC-117 IFU: turn off device before unplugging | XTC-36 IFU: Device turned off (TC-117) | 2020/04/02 | 2020/04/02 09:18:56 | passed
SPEC-134 IFU: ventilator settings | XTC-39 IFU: Upper en lower limit of the ventilator settings (TC-135) | 2020/04/02 | 2020/04/02 09:24:30 | passed
SPEC-135 IFU: Explanation of the alarms | XTC-41 IFU: explanation of the alarms (TC-136) | 2020/04/02 | 2020/04/02 09:29:07 | passed
SPEC-137 IFU: HEPA filter | XTC-44 IFU: Instructions about the use of the HEPA-filter (TC-137) | 2020/04/02 | 2020/04/02 09:37:05 | passed
SPEC-51 IFU: Instructions for correct and safe maintanance | XTC-80 IFU: Maintanance (TC-44) | 2020/04/07 | 2020/04/07 08:02:10 | passed

(OperationAIR) | Date: 2020/04/29 14:28:42
Document: 4.1 | Page: 9 / 75
Item | Tested By | Execution Date | Last Modification | Test Result
SPEC-138 IFU: alarm boundaries | XTC-45 IFU: How to set the upper and lower boundaries of the alarms (TC-138) | 2020/04/02 | 2020/04/02 09:40:54 | passed with deviation
SPEC-17 Training and clear IFU for the users | XTC-67 IFU: trained user (TC-75) | 2020/04/06 | 2020/04/06 10:01:52 | passed
| XTC-110 Usability test (TC-65) | 2020/04/10 | 2020/04/24 09:47:51 | documentation
SPEC-49 IFU: checked by experts | XTC-136 IFU Review (TC-43) | 2020/04/29 | 2020/04/29 09:52:20 | passed
SPEC-151 Label: regulatory requirements | XTC-137 Label: regulatory requirements (TC-164) | 2020/04/28 | 2020/04/29 09:54:13 | passed
SPEC-64 Emergency use sticker | XTC-13 Labeling: Warning Sticker (TC-105) | 2020/03/31 | 2020/03/31 16:01:10 | passed
SPEC-115 Emergency number on label | XTC-12 Sticker with emergency number on device (TC-113) | 2020/03/31 | 2020/03/31 15:58:50 | passed
SPEC-133 HEPA filter warning sticker | XTC-126 HEPA filter warning sticker (TC-173) | 2020/04/24 | 2020/04/24 10:34:53 | passed
SPEC-61 Do not push warning | XTC-11 Do not push warning (TC-129) | 2020/03/31 | 2020/03/31 15:58:06 | passed
SPEC-154 Fire warning sticker | XTC-108 INSPECT: Information about fire hazard on the label (TC-166) | 2020/04/20 | 2020/04/20 10:42:28 | passed
SPEC-148 Device label | XTC-121 Visiblility of label (TC-160) | 2020/04/24 | 2020/04/24 09:49:13 | passed
SPEC-130 Intuitive for use - training | XTC-78 Intuitive for use - training (TC-131) | 2020/04/06 | 2020/04/06 19:01:40 | passed
SPEC-48 Vocabulary and Semantics | XTC-138 Vocabulary and Semantics (TC-71) | 2020/04/29 | 2020/04/29 09:55:30 | passed
SPEC-167 Open Source | XTC-133 Open Source (TC-175) | 2020/04/24 | 2020/04/24 14:05:27 | passed
SPEC-124 Pre-Set Controls | XTC-83 Pre-Set Controls (TC-125) | 2020/04/07 | 2020/04/07 09:00:46 | passed
SPEC-121 Battery Housing | XTC-104 Battery Housing (TC-122) | 2020/04/13 | 2020/04/13 12:21:08 | passed
SPEC-112 Incorrect output | XTC-84 Incorrect output (TC-98) | 2020/04/07 | 2020/04/07 09:02:13 | passed
SPEC-111 Indication of parameters relevant to safety | XTC-88 Indication of parameters relevant to safety (TC-97) | 2020/04/07 | 2020/04/07 09:22:04 | passed

(OperationAIR) | Date: 2020/04/29 14:28:42
Document: 4.1 | Page: 10 / 75
Item | Tested By | Execution Date | Last Modification | Test Result
SPEC-110 Intentional exceeding of safety limits | XTC-100 Intentional exceeding of safety limits (TC-96) | 2020/04/10 | 2020/04/10 08:07:54 | passed
SPEC-109 Alarm systems | XTC-24 Alarmsystems (TC-95) | 2020/04/01 | 2020/04/01 15:26:10 | passed
SPEC-108 Usability | XTC-89 Usability (TC-94) | 2020/04/07 | 2020/04/07 09:28:25 | passed with deviation
SPEC-107 Accuracy of controls and instruments | XTC-90 Accuracy of controls and instruments (TC-93) | 2020/04/07 | 2020/04/07 11:21:34 | passed
SPEC-105 Compatibility with substances | XTC-8 Compatibility with substances (TC-90) | 2020/03/30 | 2020/03/30 08:22:16 | passed
SPEC-102 Flammable agent | XTC-7 ME intended for use in conjunction with flammable agent (TC-88) | 2020/03/30 | 2020/03/30 08:21:17 | passed
SPEC-77 Arangements of controls and indicators | XTC-105 Arrangements of controls and indicators (TC-59) | 2020/04/13 | 2020/04/13 12:24:03 | passed
SPEC-76 Electromagnetic compatibility | XTC-122 Electromagnetic compatibility (TC-58) | 2020/04/24 | 2020/04/24 09:50:16 | passed

### TEST REPORTS

XTC-32 IFU: Not for use during transport (TC-12) INSPECTION
Warning in IFU that device is not to be used during transport

1

Version 1.0 of the IFU.

Legal OperationAIR

2020/04/02

passed

Page 19 under section 10.

(OperationAIR) | Date: 2020/04/29 14:28:42
Document: 4.1 | Page: 11 / 75
Step | Action Result | Expected Result | Passed/Failed | Comment
1 | Inspect Instructions For Use | Contains a warning that device is not to be used during transport | passed

XTC-33 IFU: Check device before use (TC-13)
INSPECTION
IFU contains information on what inspection must be done before use

1

Version 1.0 of the IFU

Legal OperationAIR

2020/04/02

passed

Page 13 under section 5 subsection 1.

Step | Action Result | Expected Result | Passed/Failed | Comment
1 | Inspect instructions for use | contains information on inspections to be done before using the device | passed

XTC-34 Tidal volume range (TC-23)
TEST
Confirm that the device is able to provide tidal volumes between 300 and 700 mL

1

2020/04/02

passed

1. tV: >> 700mL (888mL)
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

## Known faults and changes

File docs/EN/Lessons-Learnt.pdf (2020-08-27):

# Tips and Pitfalls - Team Organisation

This document describes some positive and negative situations we have experienced. This is formulated into tips and pitfalls to be shared with other initiatives.

# Tips

- Use a contact form with specific questions to categorise and create a simple overview of the companies and individuals who offered their support. If all team members have access to the replies, they can quickly search for the expertise they need amongst the respondents.
- Do not hesitate to look for external support and include new specialists in your team. As soon as we felt we could use someone with a different expertise, we asked that person to join our team. E.g. to design 3D printable components, build modules of our software, tune our pressure controllers. We experienced the easy inclusion of external expertise as a strong feature of our team.
- Be aware manufacturers may be able to produce parts you would not expect. A railway company may be able to produce the power supply.
- Focus on regulations and risk management from day one. Although the design team may feel as the most important subteam, the subteam that focus on compliance to standards, regulations and risk management is critical for clinical acceptance. .
- Use media and social media attention to make the project known amongst manufacturers. The combination of media attention we received in the beginning of our project and the use of the contact form, laid the foundation for a database of offered expertise. We still use this database today.

# Pitfalls

- Without knowing what other subteams are doing, it is inevitable that some activities are done twice. A complete team with multiple subteams that work under time pressure can do much work in a short time, as everyone focuses on their own tasks. The downside is that subteams do not have insight in each other's work, so some work can be done twice. Regular contact between subteam managers therefore is necessary to detect this inefficiency early in the process.
- Do not keep your team too much in the dark, in terms of information and updates on general progress. They do not need to know the details of every subteams activities, but daily updates on the general steps taken that day improves the team spirit.

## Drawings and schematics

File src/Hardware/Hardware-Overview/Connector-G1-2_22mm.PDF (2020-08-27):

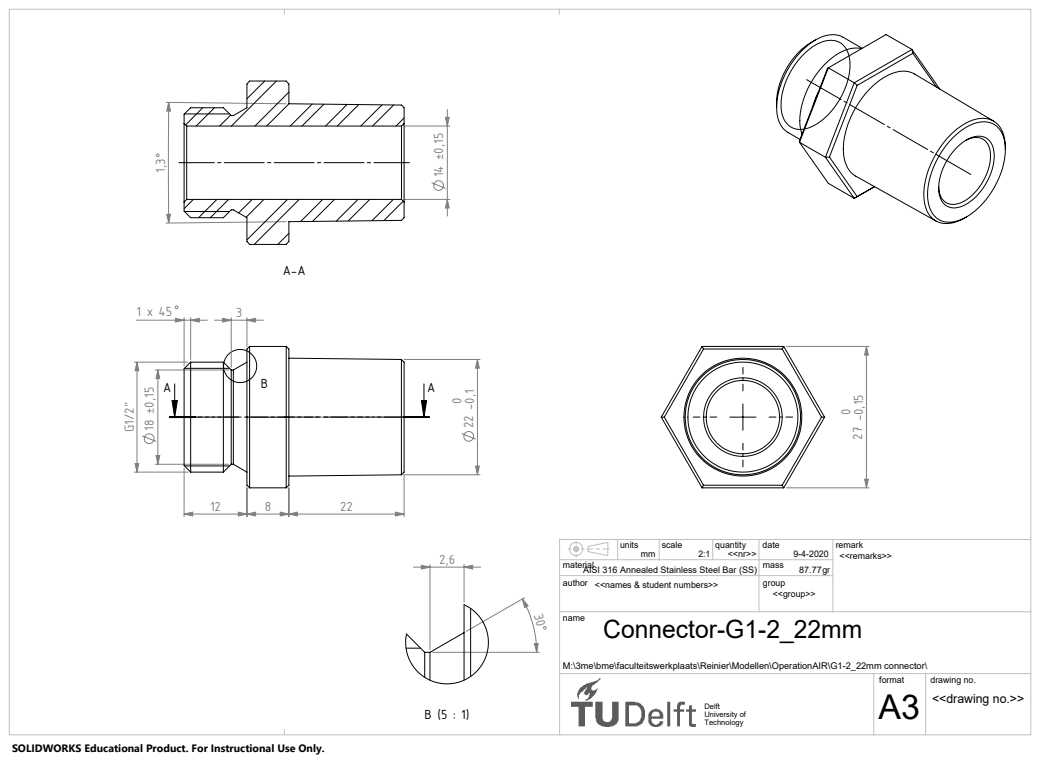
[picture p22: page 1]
format; drawing no.; <<drawing no.>>; University of

units mm | scale 2:1 | quantity <<nr>> | date 9-4-2020 | remark <<remarks>>

AISI 316 Annealed Stainless Steel Bar (SS) material | | | | 87.77 gr mass
author <<names & student numbers>> | | | | group <<group>>

M:\3me\bme\faculteitswerkplaats\Reinier\Modellen\OperationAIR\G1-2_22mm connector\

SOLIDWORKS Educational Product. For Instructional Use Only.

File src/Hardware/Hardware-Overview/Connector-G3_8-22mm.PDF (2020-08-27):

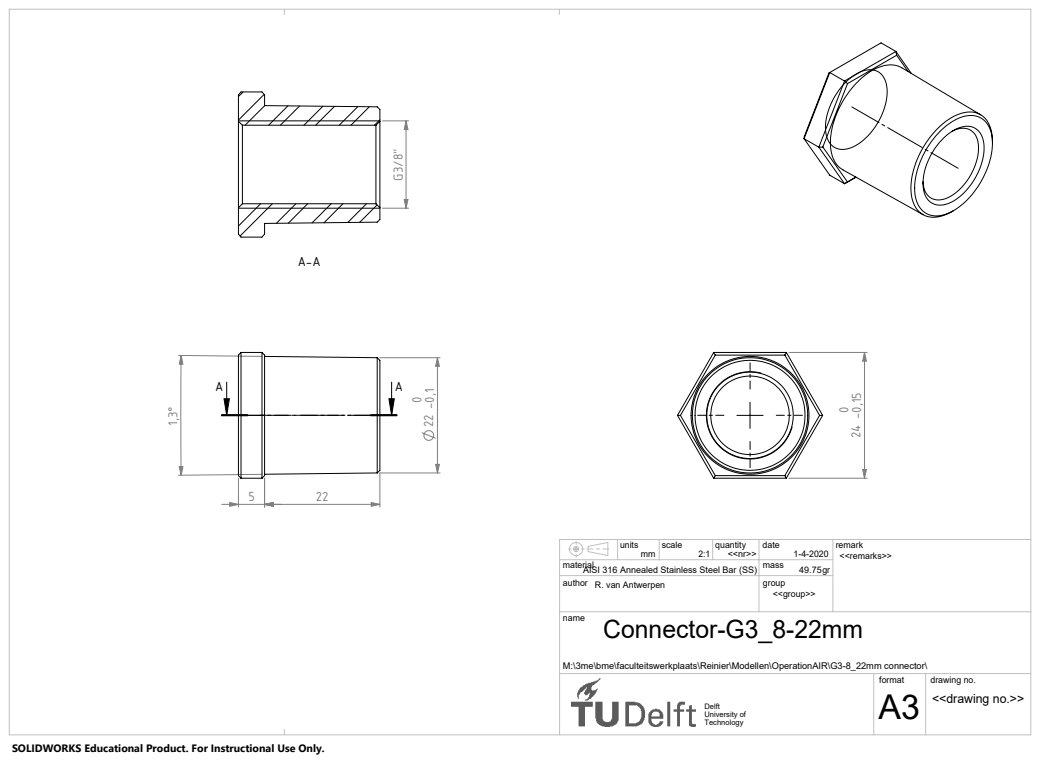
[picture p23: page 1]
format; drawing no.; <<drawing no.>>; University of

units mm | scale 2:1 | quantity <<nr>> | date 1-4-2020 | remark <<remarks>>

AISI 316 Annealed Stainless Steel Bar (SS) material | | | | 49.75 gr mass
author R. van Antwerpen | | | | group <<group>>

M:\3me\bme\faculteitswerkplaats\Reinier\Modellen\OperationAIR\G3-8_22mm connector\

SOLIDWORKS Educational Product. For Instructional Use Only.

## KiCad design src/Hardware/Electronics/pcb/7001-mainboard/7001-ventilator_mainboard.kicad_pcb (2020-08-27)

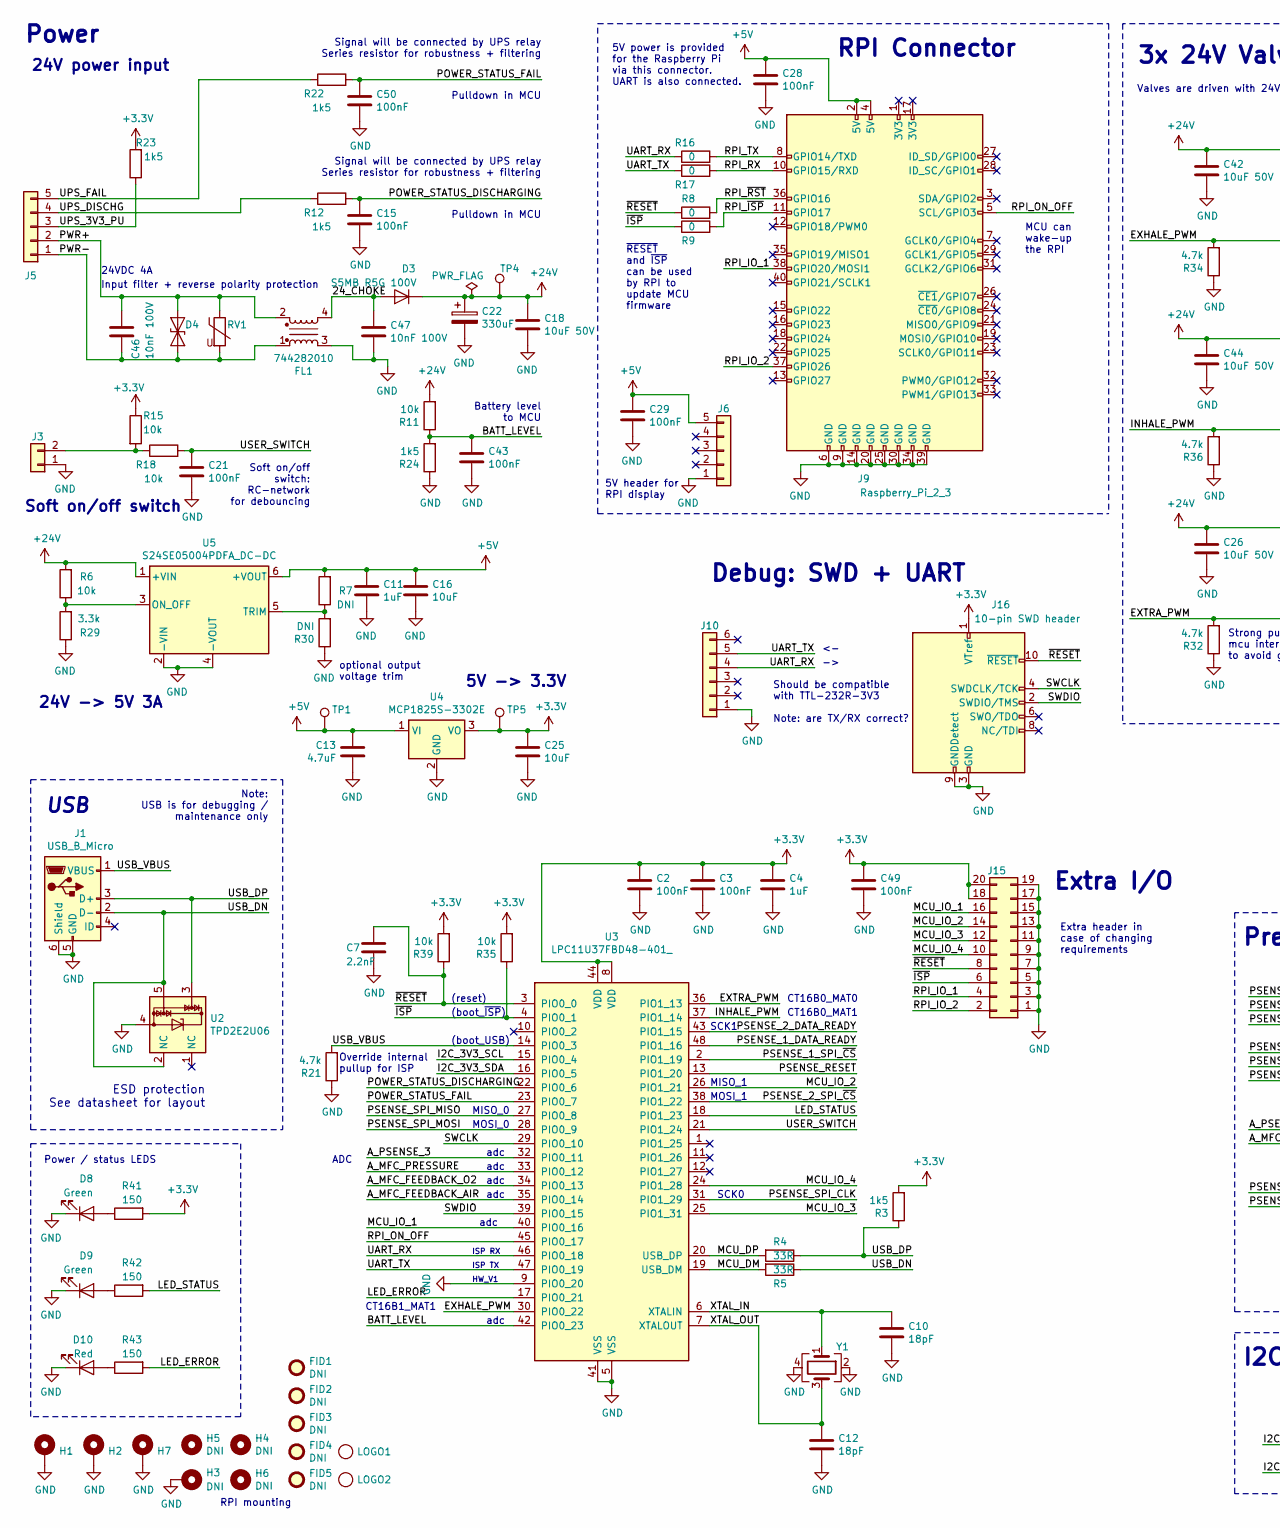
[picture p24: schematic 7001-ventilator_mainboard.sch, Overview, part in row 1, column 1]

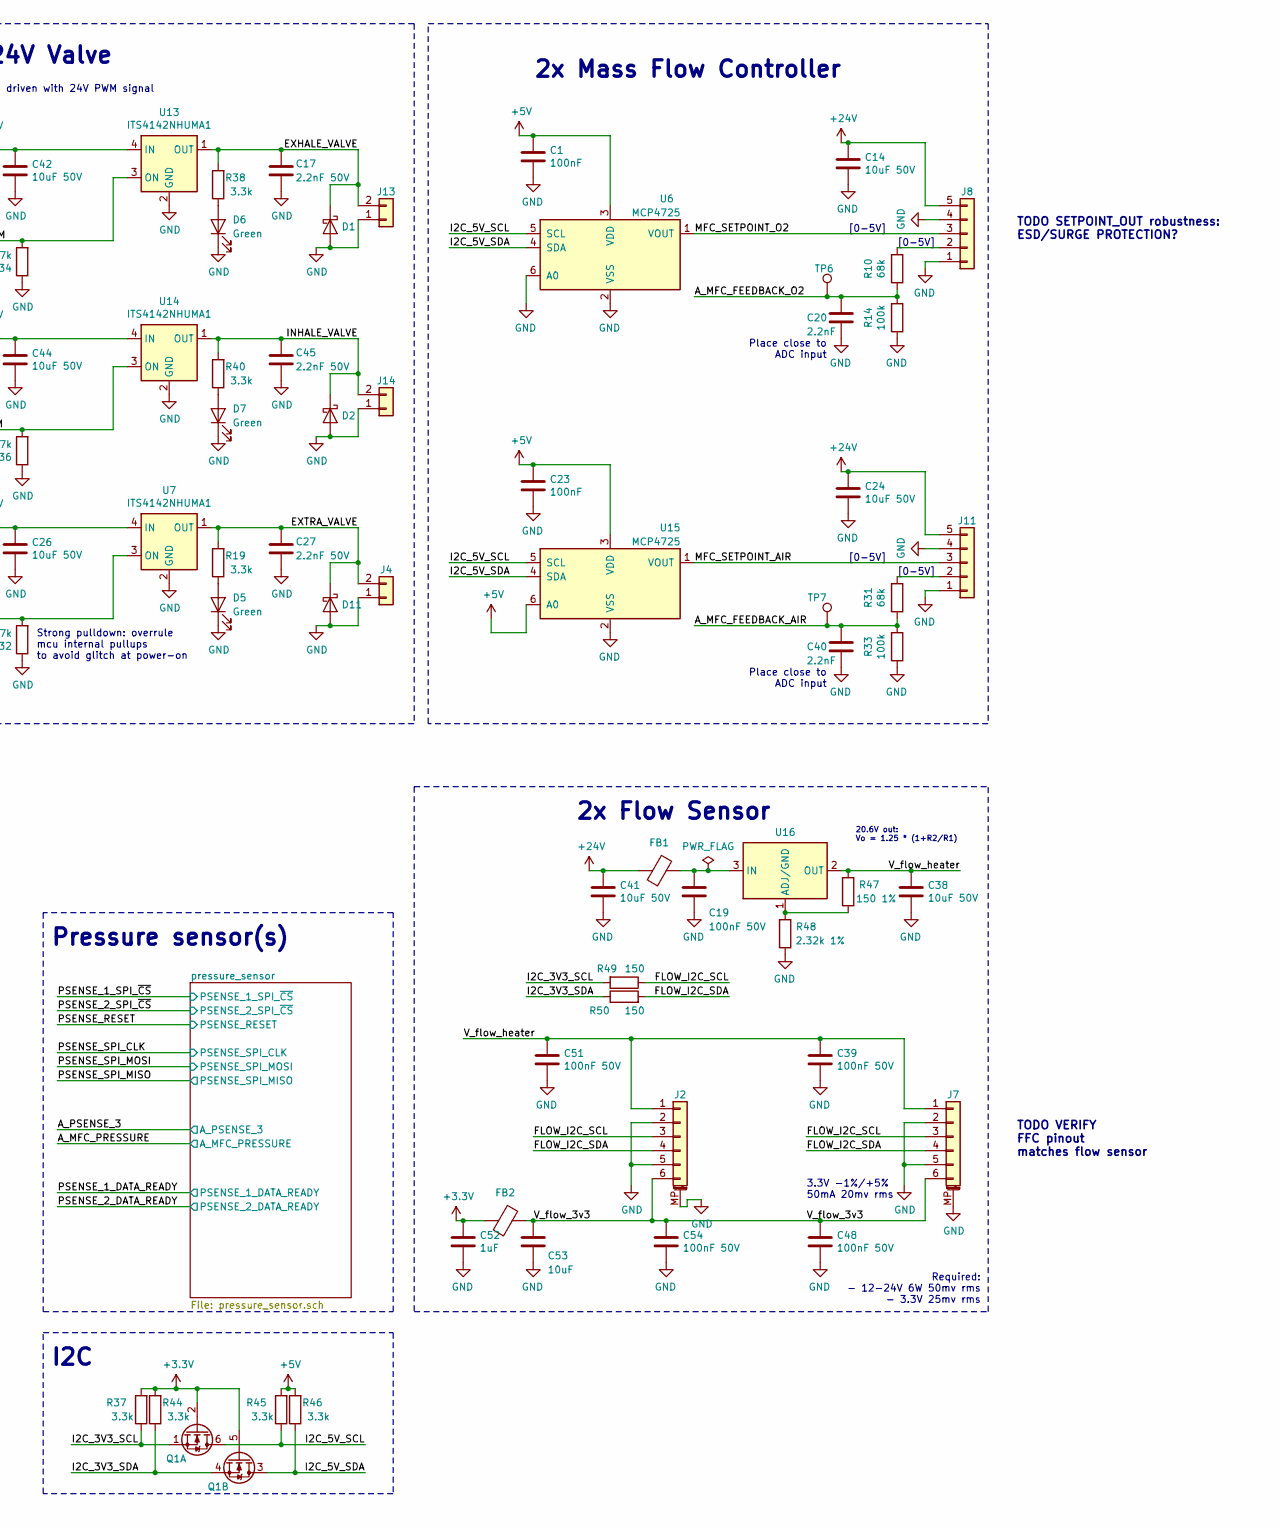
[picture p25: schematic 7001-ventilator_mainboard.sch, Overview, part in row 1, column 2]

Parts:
C1, C2, C3, C15, C21, C23, C28, C29, C43, C49, C50: 100nF; C_0805_2012Metric
C4, C11, C52: 1uF; C_0805_2012Metric
C7, C20, C40: 2.2nF; C_0805_2012Metric
C10, C12: 18pF; C_0805_2012Metric
C13: 4.7uF; C_0805_2012Metric
C14, C18, C24, C26, C38, C41, C42, C44: 10uF 50V; C_1210_3225Metric
C16, C25, C53: 10uF; C_0805_2012Metric
C17, C27, C45: 2.2nF 50V; C_0805_2012Metric
C19, C39, C48, C51, C54: 100nF 50V; C_0805_2012Metric
C22: 330uF; CP_Elec_12.5_MAL214699107E3; MPN MAL214699107E3
C46, C47: 10nF 100V; C_1206_3216Metric; MPN 885012208112
D1, D2, D11: D_Schottky; D_SOD-123F; MPN NRVTS245ESFT3G
D3: S5MB R5G 100V; D_SMB; MPN S5MB R5G
D4: D_TVS; WE-TVSP_TVS_DIODE; MPN 824501301; Farnell 2536572
D5, D6, D7, D8, D9: Green; LED_0805_2012Metric; MPN KP-2012LSGC; Farnell 2463991
D10: Red; LED_0805_2012Metric; MPN KPT-2012EC; Farnell 2099236
FB1, FB2: BLM18HE601SN1D; L_0603_1608Metric; MPN BLM18HE601SN1D; Farnell 2443238
FID1, FID2, FID3, FID4, FID5: DNI; Fiducial_1mm_Mask2mm
FL1: 744282010; L_CommonMode_Wuerth_WE-SCC; MPN 744282010
H1, H2, H7: DNI (mounting hole); MountingHole_2.7mm_M2.5_Pad__wavesolder
H3: DNI; MountingHole_2.7mm_M2.5_Pad__wavesolder
H4, H5, H6: DNI; MountingHole_2.7mm_M2.5__wavesolder
J1: USB_B_Micro; USB_Micro-B_Molex_47346-0001; MPN 47346-0001; Farnell 1568026
J2, J7: 6-pin FFC connector; Hirose_FH12-6S-0.5SH_1x06-1MP_P0.50mm_Horizontal; MPN FH12-6S-0.5SH; Farnell 1324538
J3, J4, J13, J14: 2-pin screw terminal; TerminalBlock_Wurth_WR-TBL_691322110002_1x02_P3.50mm_Horizo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; MPN 691322110002; Farnell 1841315
J5: 5-pin screw terminal vertical; TerminalBlock_Wurth_WR-TBL_691321100005_1x05_P3.50mm_Vertic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; MPN 691321100005
J6: 5V out; PinHeader_1x05_P2.54mm_Vertical
J8, J11: 5-pin screw terminal; TerminalBlock_Wurth_WR-TBL_691322110005_1x05_P3.50mm_Horizo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; MPN 691322110005
J9: Raspberry_Pi_2_3; PinSocket_2x20_P2.54mm_Vertical_holes_SMD; MPN REF-182665-01
J10: 6-pin header; PinHeader_1x06_P2.54mm_Vertical
J15: 2x10-pin header; PinHeader_2x10_P2.54mm_Vertical_SMD; MPN 61032021121
J16: 10-pin SWD header; connector_jtag_10pin_shrouded; MPN 20021521-00010T1LF
LOGO1: LOGO; JitterLogo
LOGO2: LOGO; OperationAir260
Q1: NX3020NAKV,115; SOT-666; MPN NX3020NAKV,115; Farnell 2311182
R3, R12, R22, R23, R24: 1k5; R_0805_2012Metric
R4, R5: 33R; R_0805_2012Metric
R6, R11, R15, R18, R35, R39: 10k; R_0805_2012Metric
R7, R30: DNI; R_0805_2012Metric
R8, R9, R16, R17: 0; R_0805_2012Metric
R10, R31: 68k; R_0805_2012Metric
R14, R33: 100k; R_0805_2012Metric
R19, R29, R37, R38, R40, R44, R45, R46: 3.3k; R_0805_2012Metric
R21, R32, R34, R36: 4.7k; R_0805_2012Metric
R41, R42, R43, R49, R50: 150; R_0805_2012Metric
R47: 150 1%; R_0805_2012Metric
R48: 2.32k 1%; R_0805_2012Metric
RV1: Varistor; WE_VS_Varistor; MPN 82551250
TP1, TP4, TP5, TP6, TP7: DNI; TestPoint_THTPad_D1.5mm_Drill0.7mm
U2: TPD2E2U06; SOT-553; MPN TPD2E2U06DRLR; Farnell 3116500
U3: LPC11U37FBD48-401_; LQFP-48_7x7mm_P0.5mm; MPN LPC11U37FBD48/401; Farnell 2115662
U4: MCP1825S-3302E; SOT-223-3_TabPin2; MPN MCP1825S-3302E; Farnell 1578404
U5: S24SE05004PDFA_DC-DC; DCDC-5V_S24SE05004PDFA; MPN S24SE05004PDFA; Mouser 108-S24SE05004PDFA
U6, U15: MCP4725; SOT-23-6; MPN MCP4725A1T-E/CH; Farnell 2774927
U7, U13, U14: ITS4142NHUMA1; SOT-223; MPN ITS4142NHUMA1
U16: LD1086DTTR; TO-252-2; MPN LD1086DTTR (adjustable)
Y1: 12MHz; Crystal_SMD_3225-4Pin_3.2x2.5mm; MPN 7M-12.000MEEQ-T; Farnell 2308719

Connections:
+3V3: C2.1, C3.1, C4.1, C25.1, C49.1, C52.1, FB2.2, J15.18, J15.20, J16.1 (VTref), Q1.2 (G), Q1.5 (G), R3.2, R15.1, R23.2, R35.2, R37.2, R39.2, R41.2, R44.2, TP5.1, U3.8 (VDD), U3.44 (VDD), U4.3 (VO); also elsewhere on the board
+5V: C1.1, C11.1, C13.1, C16.1, C23.1, C28.1, C29.1, J6.5, J9.2 (5V), J9.4 (5V), R7.2, R45.2, R46.2, TP1.1, U4.1 (VI), U5.6 (+VOUT), U6.3 (VDD), U15.3 (VDD), U15.6 (A0); also elsewhere on the board
+24V: C14.1, C18.1, C22.1, C24.1, C26.1, C41.1, C42.1, C44.1, D3.1 (K), FB1.2, J8.5, J11.5, R6.2, R11.2, TP4.1, U5.1 (+VIN), U7.4 (IN), U13.4 (IN), U14.4 (IN)
/24_CHOKE: C47.1, D3.2 (A), FL1.4
/A_MFC_FEEDBACK_AIR: C40.1, R31.1, R33.2, TP7.1, U3.35 (PIO0_14)
/A_MFC_FEEDBACK_O2: C20.1, R10.1, R14.2, TP6.1, U3.34 (PIO0_13)
/A_MFC_PRESSURE: U3.33 (PIO0_12); also elsewhere on the board
/A_PSENSE_3: U3.32 (PIO0_11); also elsewhere on the board
/BATT_LEVEL: C43.1, R11.1, R24.2, U3.42 (PIO0_23)
/EXHALE_PWM: R34.2, U3.30 (PIO0_22), U13.3 (ON)
/EXHALE_VALVE: C17.1, D1.1 (K), J13.2, R38.2, U13.1 (OUT)
/EXTRA_PWM: R32.2, U3.36 (PIO1_13), U7.3 (ON)
/EXTRA_VALVE: C27.1, D11.1 (K), J4.2, R19.2, U7.1 (OUT)
/FLOW_I2C_SCL: J2.3, J7.3, R49.1
/FLOW_I2C_SDA: J2.4, J7.4, R50.2
/I2C_3V3_SCL: Q1.1 (S), R37.1, R49.2, U3.15 (PIO0_4)
/I2C_3V3_SDA: Q1.4 (S), R44.1, R50.1, U3.16 (PIO0_5)
/I2C_5V_SCL: Q1.6 (D), R45.1, U6.5 (SCL), U15.5 (SCL)
/I2C_5V_SDA: Q1.3 (D), R46.1, U6.4 (SDA), U15.4 (SDA)
/INHALE_PWM: R36.2, U3.37 (PIO1_14), U14.3 (ON)
/INHALE_VALVE: C45.1, D2.1 (K), J14.2, R40.2, U14.1 (OUT)
/LED_ERROR: R43.2, U3.17 (PIO0_21)
/LED_STATUS: R42.2, U3.18 (PIO1_23)
/MCU_DM: R5.2, U3.19 (USB_DM)
/MCU_DP: R4.2, U3.20 (USB_DP)
/MCU_IO_1: J15.16, U3.40 (PIO0_16)
/MCU_IO_2: J15.14, U3.26 (PIO1_21)
/MCU_IO_3: J15.12, U3.25 (PIO1_31)
/MCU_IO_4: J15.10, U3.24 (PIO1_28)
/MFC_SETPOINT_AIR: J11.3, U15.1 (VOUT)
/MFC_SETPOINT_O2: J8.3, U6.1 (VOUT)
/POWER_STATUS_DISCHARGING: C15.1, R12.2, U3.22 (PIO0_6)
/POWER_STATUS_FAIL: C50.1, R22.2, U3.23 (PIO0_7)
/PSENSE_1_DATA_READY: U3.48 (PIO1_16); also elsewhere on the board
/PSENSE_1_SPI_~CS~: U3.2 (PIO1_19); also elsewhere on the board
/PSENSE_2_DATA_READY: U3.43 (PIO1_15); also elsewhere on the board
/PSENSE_2_SPI_~CS~: U3.38 (PIO1_22); also elsewhere on the board
/PSENSE_RESET: U3.13 (PIO1_20); also elsewhere on the board
/PSENSE_SPI_CLK: U3.31 (PIO1_29); also elsewhere on the board
/PSENSE_SPI_MISO: U3.27 (PIO0_8); also elsewhere on the board
/PSENSE_SPI_MOSI: U3.28 (PIO0_9); also elsewhere on the board
/PWR+: C46.1, D4.2 (A2), FL1.2, J5.2, RV1.1
/PWR-: C46.2, D4.1 (A1), FL1.1, J5.1, RV1.2
/RPI_IO_1: J9.38 (GPIO20/MOSI1), J15.4
/RPI_IO_2: J9.37 (GPIO26), J15.2
/RPI_ON_OFF: J9.5 (SCL/GPIO3), U3.45 (PIO0_17)
/RPI_RX: J9.10 (GPIO15/RXD), R17.2
/RPI_TX: J9.8 (GPIO14/TXD), R16.2
/RPI_~ISP~: J9.11 (GPIO17), R9.2
/RPI_~RST~: J9.36 (GPIO16), R8.2
/SWCLK: J16.4 (SWDCLK/TCK), U3.29 (PIO0_10)
/SWDIO: J16.2 (SWDIO/TMS), U3.39 (PIO0_15)
/UART_RX: J10.4, R16.1, U3.46 (PIO0_18)
/UART_TX: J10.5, R17.1, U3.47 (PIO0_19)
/UPS_3V3_PU: J5.3, R23.1
/UPS_DISCHG: J5.4, R12.1
/UPS_FAIL: J5.5, R22.1
/USB_DN: J1.2 (D-), R5.1, U2.2 (NC), U2.5
/USB_DP: J1.3 (D+), R3.1, R4.1, U2.3
/USB_VBUS: J1.1 (VBUS), R21.2, U3.14 (PIO0_3)
/USER_SWITCH: C21.1, R18.2, U3.21 (PIO1_24)
/V_flow_3v3: C48.1, C53.1, C54.1, FB2.1, J2.6, J7.6
/V_flow_heater: C38.1, C39.1, C51.1, J2.1, J7.1, R47.2, U16.2 (OUT)
/XTAL_IN: C10.1, U3.6 (XTALIN), Y1.1
/XTAL_OUT: C12.1, U3.7 (XTALOUT), Y1.3
/~ISP~: J15.6, R9.1, R35.1, U3.4 (PIO0_1)
/~RESET~: C7.1, J15.8, J16.10 (~RESET~), R8.1, R39.1, U3.3 (PIO0_0)
GND: C1.2, C2.2, C3.2, C4.2, C7.2, C10.2, C11.2, C12.2, C13.2, C14.2, C15.2, C16.2, C17.2, C18.2, C19.2, C20.2, C21.2, C22.2, C23.2, C24.2, C25.2, C26.2, C27.2, C28.2, C29.2, C38.2, C39.2, C40.2, C41.2, C42.2, C43.2, C44.2, C45.2, C47.2, C48.2, C49.2, C50.2, C51.2, C52.2, C53.2, C54.2, D1.2 (A), D2.2 (A), D5.1 (K), D6.1 (K), D7.1 (K), D8.1 (K), D9.1 (K), D10.1 (K), D11.2 (A), FL1.3, H1.1, H2.1, H3.1, H7.1, J1.5 (GND), J1.6 (Shield), J2.2, J2.5, J2.MP (MountPin), J3.1, J4.1, J6.1, J7.2, J7.5, J7.MP (MountPin), J8.1, J8.4, J9.6 (GND), J9.9 (GND), J9.14 (GND), J9.20 (GND), J9.25 (GND), J9.30 (GND), J9.34 (GND), J9.39 (GND), J10.1, J11.1, J11.4, J13.1, J14.1, J15.1, J15.3, J15.5, J15.7, J15.9, J15.11, J15.13, J15.15, J15.17, J15.19, J16.3 (GND), J16.5 (GND), J16.9 (GNDDetect), R14.1, R21.1, R24.1, R29.1, R30.1, R32.1, R33.1, R34.1, R36.1, R48.1, U2.4, U3.5 (VSS), U3.9 (PIO0_20), U3.41 (VSS), U4.2 (GND), U5.2 (-VIN), U5.4 (-VOUT), U6.2 (VSS), U6.6 (A0), U7.2 (GND), U13.2 (GND), U14.2 (GND), U15.2 (VSS), Y1.2, Y1.4; also elsewhere on the board
unnamed: C19.1, FB1.1, U16.3 (IN)
unnamed: D5.2 (A), R19.1
unnamed: D6.2 (A), R38.1
unnamed: D7.2 (A), R40.1
unnamed: D8.2 (A), R41.1
unnamed: D9.2 (A), R42.1
unnamed: D10.2 (A), R43.1
unnamed: J3.2, R15.2, R18.1
unnamed: J8.2, R10.2
unnamed: J11.2, R31.2
unnamed: R6.1, R29.2, U5.3 (ON_OFF)
unnamed: R7.1, R30.2, U5.5 (TRIM)
unnamed: R47.1, R48.2, U16.1 (ADJ/GND)

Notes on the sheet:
5V header for RPI display
5V -> 3.3V
24VDC 4A
24V -> 5V 3A
24V power input
Power
Pressure sensor(s)
optional output voltage trim
3x 24V Valve
Input filter + reverse polarity protection
Required: - 12-24V 6W 50mv rms - 3.3V 25mv rms
3.3V -1%/+5% 50mA 20mv rms
Valves are driven with 24V PWM signal
Place close to ADC input
2x Mass Flow Controller
2x Flow Sensor
RPI Connector
Signal will be connected by UPS relay Series resistor for robustness + filtering
TODO SETPOINT_OUT robustness: ESD/SURGE PROTECTION?
Strong pulldown: overrule mcu internal pullups to avoid glitch at power-on
SCK1
MOSI_1
MISO_1
SCK0
MISO_0
MOSI_0
adc
Extra I/O
Power / status LEDS
Should be compatible with TTL-232R-3V3 Note: are TX/RX correct?
CT16B0_MAT0
CT16B1_MAT1
CT16B0_MAT1
RPI mounting
Debug: SWD + UART
ADC
USB
(reset)
(boot_USB)
(boot_~ISP~)

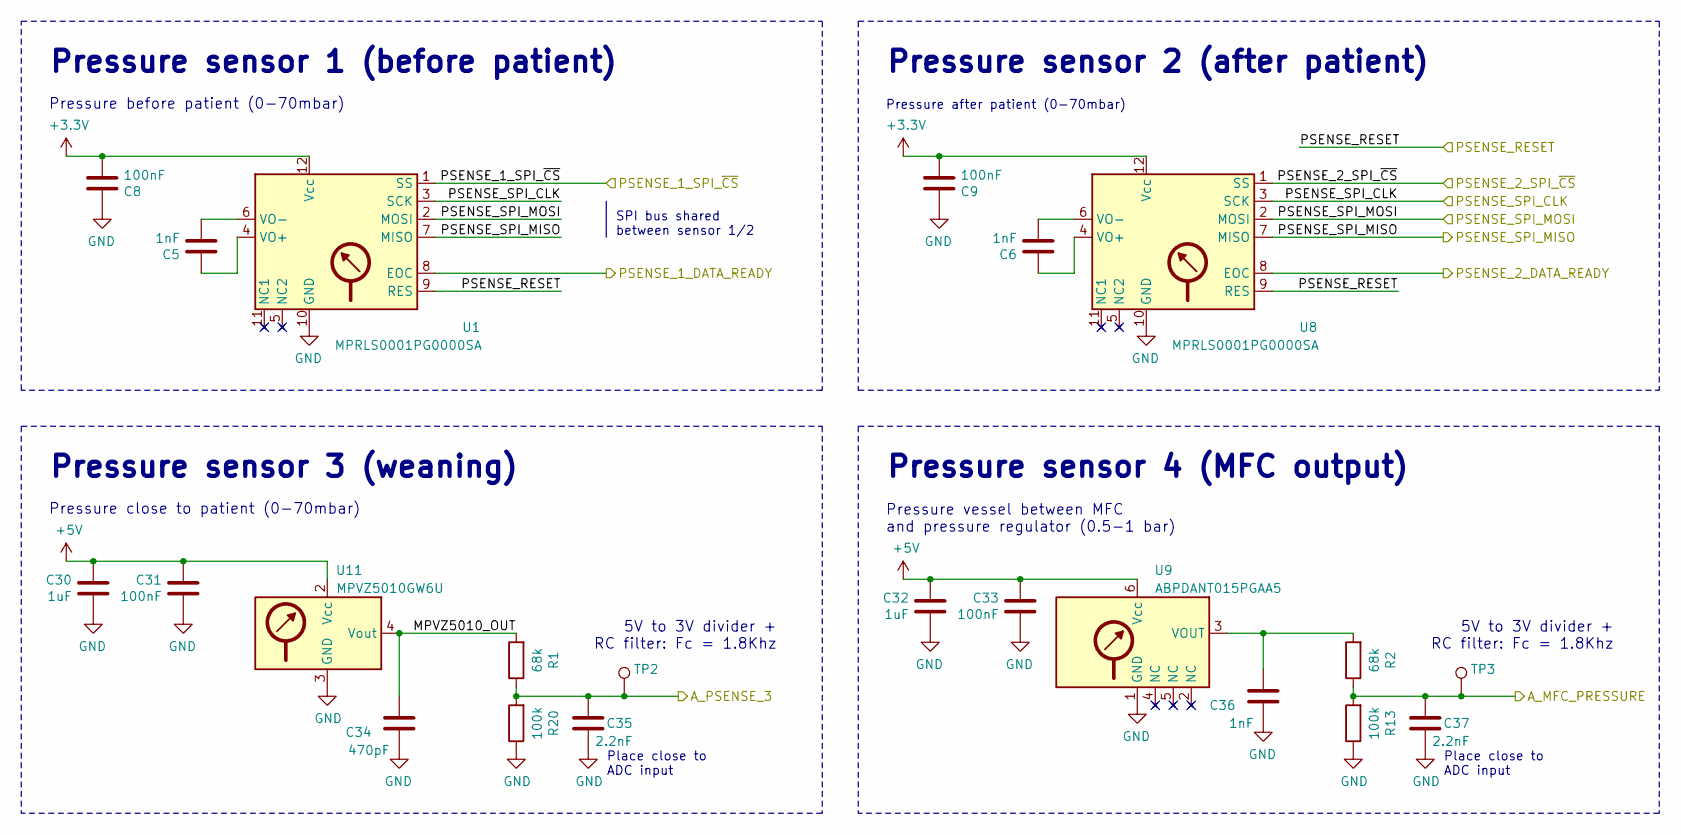
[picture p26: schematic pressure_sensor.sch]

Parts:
C5, C6, C36: 1nF; C_0805_2012Metric
C8, C9, C31, C33: 100nF; C_0805_2012Metric
C30, C32: 1uF; C_0805_2012Metric
C34: 470pF; C_0805_2012Metric
C35, C37: 2.2nF; C_0805_2012Metric
R1, R2: 68k; R_0805_2012Metric
R13, R20: 100k; R_0805_2012Metric
TP2, TP3: DNI; TestPoint_THTPad_D1.5mm_Drill0.7mm
U1, U8: MPRLS0001PG0000SA; MPN MPRLS0001PG0000SA; Digikey 480-7100-1-ND
U9: ABPDXXX000XXAX5; ABPDXXX000XX0XX; MPN ABPDANT015PGAA5; Digikey 480-6253-ND
U11: MPVZ5010GW6U; MPN MPVZ5010GW6U

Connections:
+3V3: C8.2, C9.2, U1.12 (Vcc), U8.12 (Vcc); also elsewhere on the board
+5V: C30.1, C31.1, C32.1, C33.1, U9.6 (Vcc), U11.2 (Vcc); also elsewhere on the board
/A_MFC_PRESSURE: C37.1, R2.1, R13.2, TP3.1; also elsewhere on the board
/A_PSENSE_3: C35.1, R1.1, R20.2, TP2.1; also elsewhere on the board
/PSENSE_1_DATA_READY: U1.8 (EOC); also elsewhere on the board
/PSENSE_1_SPI_~CS~: U1.1 (SS); also elsewhere on the board
/PSENSE_2_DATA_READY: U8.8 (EOC); also elsewhere on the board
/PSENSE_2_SPI_~CS~: U8.1 (SS); also elsewhere on the board
/PSENSE_RESET: U1.9 (RES), U8.9 (RES); also elsewhere on the board
/PSENSE_SPI_CLK: U1.3 (SCK), U8.3 (SCK); also elsewhere on the board
/PSENSE_SPI_MISO: U1.7 (MISO), U8.7 (MISO); also elsewhere on the board
/PSENSE_SPI_MOSI: U1.2 (MOSI), U8.2 (MOSI); also elsewhere on the board
/pressure_sensor/MPVZ5010_OUT: C34.1, R1.2, U11.4 (Vout)
GND: C8.1, C9.1, C30.2, C31.2, C32.2, C33.2, C34.2, C35.2, C36.2, C37.2, R13.1, R20.1, U1.10 (GND), U8.10 (GND), U9.1 (GND), U11.3 (GND); also elsewhere on the board
unnamed: C5.1, U1.4 (VO+)
unnamed: C5.2, U1.6 (VO-)
unnamed: C6.1, U8.4 (VO+)
unnamed: C6.2, U8.6 (VO-)
unnamed: C36.1, R2.2, U9.3 (VOUT)

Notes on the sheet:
Pressure after patient (0-70mbar)
Pressure before patient (0-70mbar)
Pressure sensor 2 (after patient)
Pressure sensor 1 (before patient)
SPI bus shared between sensor 1/2
Pressure sensor 3 (weaning)
Pressure close to patient (0-70mbar)
Place close to ADC input
5V to 3V divider + RC filter: Fc = 1.8Khz
Pressure vessel between MFC and pressure regulator (0.5-1 bar)
Pressure sensor 4 (MFC output)

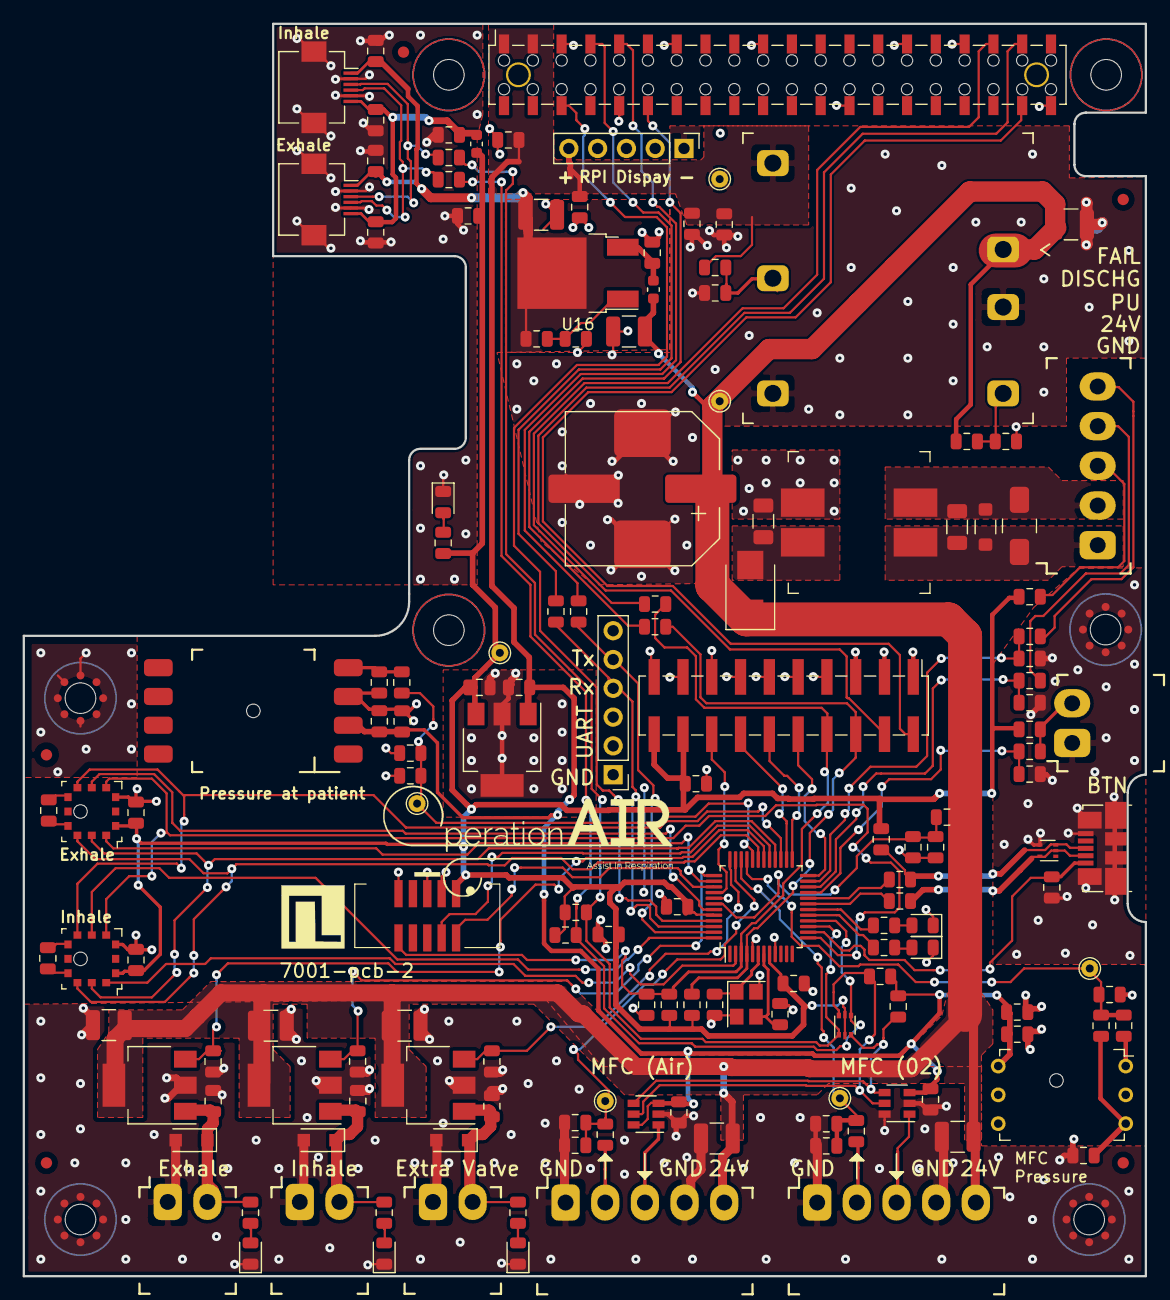
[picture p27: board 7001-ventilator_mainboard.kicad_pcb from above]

Board: 2 copper layers, 99.0 x 110.5 mm, 167 parts (0 on the bottom side), 87 nets.
